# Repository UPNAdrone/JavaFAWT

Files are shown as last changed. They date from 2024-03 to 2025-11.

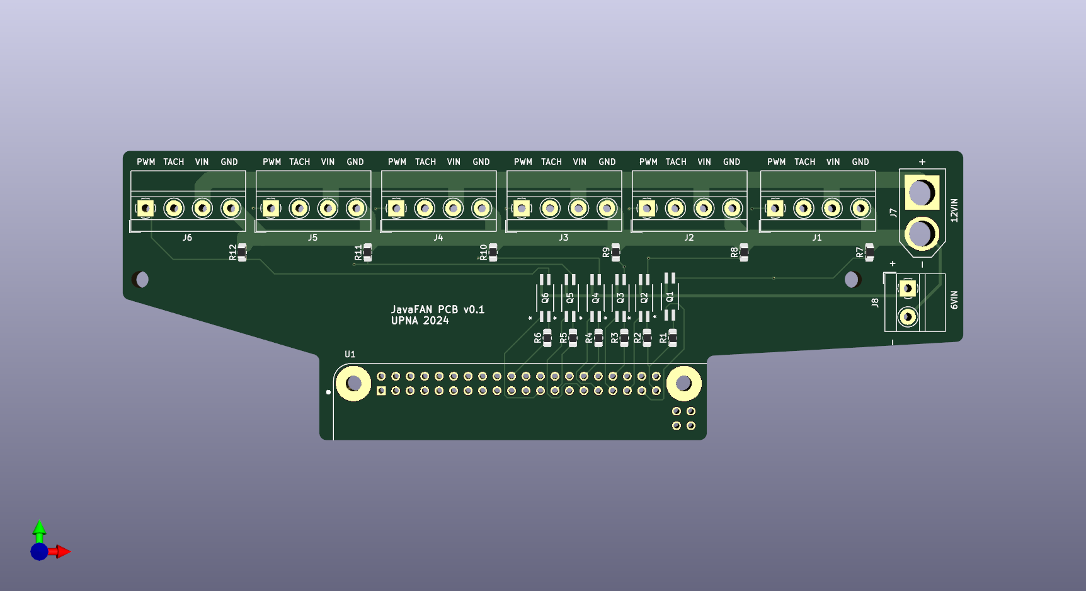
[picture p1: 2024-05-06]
hardware/module/electronics/pcb-test.png

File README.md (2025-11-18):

# JavaFAWT
JavaFAWT is a fan-array-wind tunnel (FAWT) open-source software and hardware architecture developed by the drones lab of Universidad Pública de Navarra. It includes diagrams and PCB layouts for electronics, CAD designs for hardware, and source files for running and adapting the software. 
## Introduction


The proposed control scheme follows a wireless server-client architecture. A Java GUI is provided for the control station (server) to connect and command each fan, organized in series of modules. Each module is managed by a single Raspberry Pi client (currently tested with Raspberry Pi 3, 4, Zero 2 w), which receives the fan speed control messages from the server via a wireless WebSocket. The client receives the message, identifies its connected fans, and converts the speed signal to a PWM output for each fan, allowing for precise individual control of an indefinite number of fans. Thanks to the custom PCB interface, an external power supply can be used for each module, and a single control power source is used to elevate the 3.3V PWM control signal for each and every fan up to a standard required voltage.

### Features
* Modular low-cost FAWT architecture.
* Individual or multiple fan speed control through a simple unified interface.
* Websockets protocol implemented for wireless communication with each fan module.
* User-programmable automatic speed sequences via .CSV files for repeatability and reproducibility of experiments.

## Relevant links
Bill of Materials (BOM) can be found [here](https://github.com/UPNAdrone/JavaFAWT/blob/main/hardware/Bill%20of%20Materials.xlsx)

PCB Manufacturing project can be found [here](https://www.pcbway.com/project/shareproject/JavaFAWT_PCB_v0_1_1426b5d5.html)

## How to install & run
Detailed instructions for installing and running the software can be found [here](https://github.com/UPNAdrone/JavaFAWT/blob/main/documentation/private/docs/installation.md).

A Tutorial/Manual of use can be found [here](https://github.com/UPNAdrone/JavaFAWT/blob/main/documentation/private/docs/installation.md).

## Files structure
- Documentation
  - private
    - docs -> .md files for generating public documentation site.
    - site -> compiled documentation website for dev purposes.
  - public -> compiled documentation website for public purposes.
- Examples -> provided examples.
- Hardware
  - module -> All the components required to assemble a single module.
  - testing_equipment -> Other components developed for testing.
- Software
  - clientCode -> Python PWM client
  - functionalities -> example functionalities provided for automatic fan control.
  - pythonCode -> Python client file for controlling the fans from the Raspberry Pi.
  - serverCode -> JavaFAWT server software.

## Dataset for inverse flow control
Our recorded dataset consists of approximately 45,176 samples recorded with our experimental 6x4 wind tunnel. It includes two CSV files: one for relative pressures (directly extracted from the nanoDAQ LTS-32 pressure scanner readings), one for velocities (extracted by converting the relative pressure, temperature and density values to velocity). The dataset can be found in Hugging Face: [https://huggingface.co/datasets/UPNAdrone/WindTunnel](https://huggingface.co/datasets/UPNAdrone/WindTunnel)

## Work in progress
* Fan speed feedback is currenly under development.
  
## Licensing
JavaFAWT is made available under the [MIT License](https://opensource.org/licenses/MIT). You are free to use, modify, and distribute this module in accordance with the terms of the MIT License.

### Reference and Citation
If you use this module for research, please consider citing our paper to acknowledge its contribution:

```bibtex
@article{pending,
  title={},
  author={},
  journal={},
  volume={},
  pages={},
  year={},
  publisher={}
}
```

---



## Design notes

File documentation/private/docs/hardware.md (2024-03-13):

# How to build a FAWT

URL example: [mkdocs.org](https://www.mkdocs.org).

## Commands

* `mkdocs new [dir-name]` - Create a new project.
* `mkdocs serve` - Start the live-reloading docs server.
* `mkdocs build` - Build the documentation site.
* `mkdocs -h` - Print help message and exit.

## Project layout

    mkdocs.yml    # The configuration file.
    docs/
        index.md  # The documentation homepage.
        ...       # Other markdown pages, images and other files.

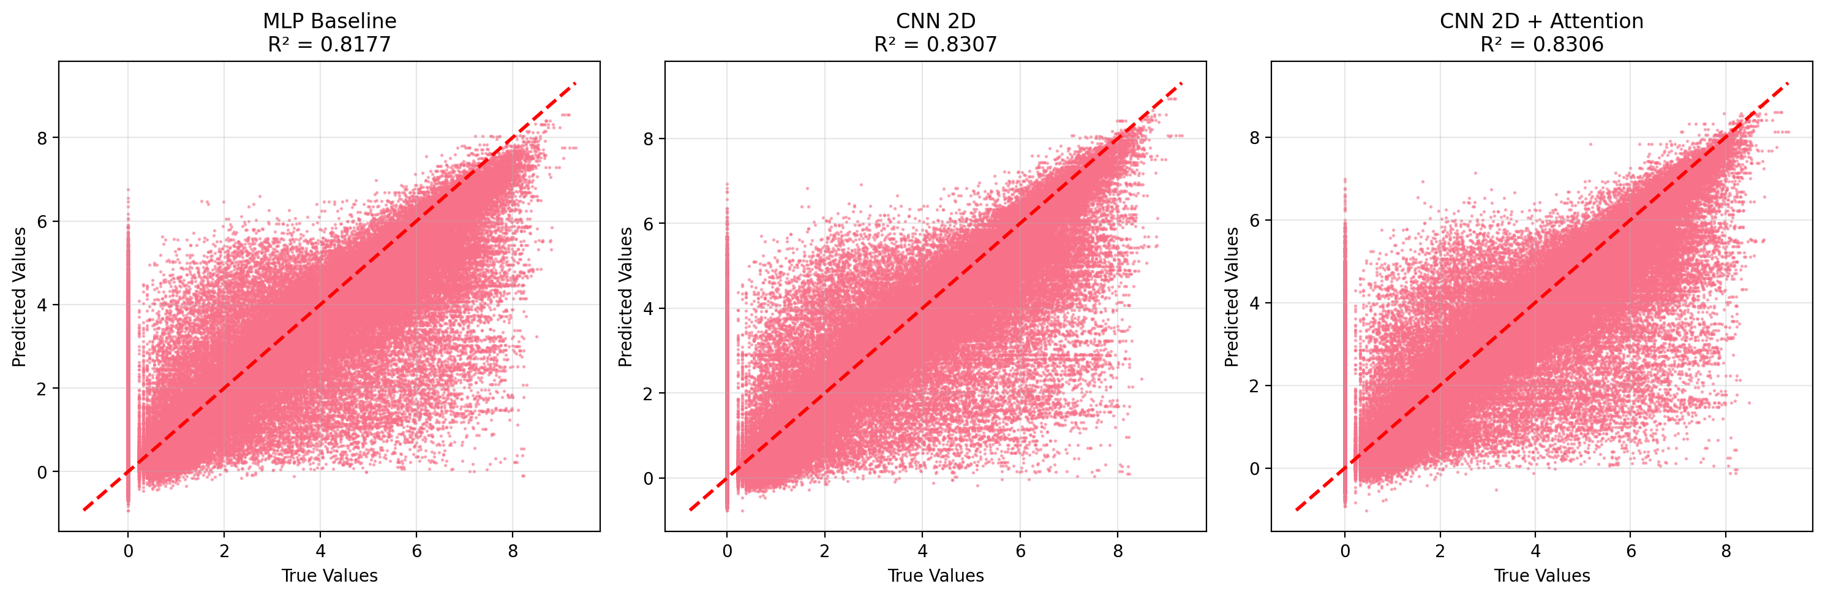
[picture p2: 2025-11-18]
inverse_control/unified_comparison/predictions_vs_true.png

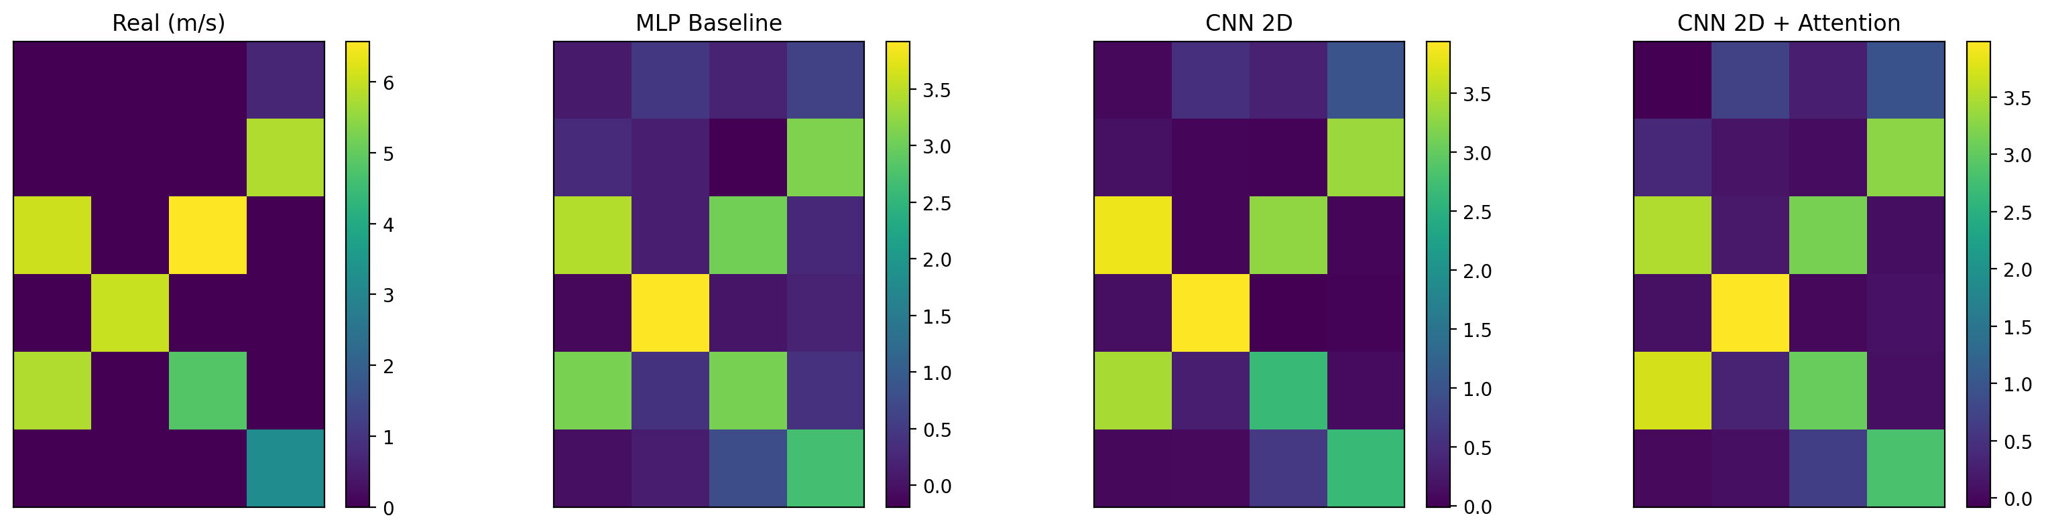
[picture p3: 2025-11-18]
inverse_control/unified_comparison/18cm/sample_heatmaps_7_idx_6357.png

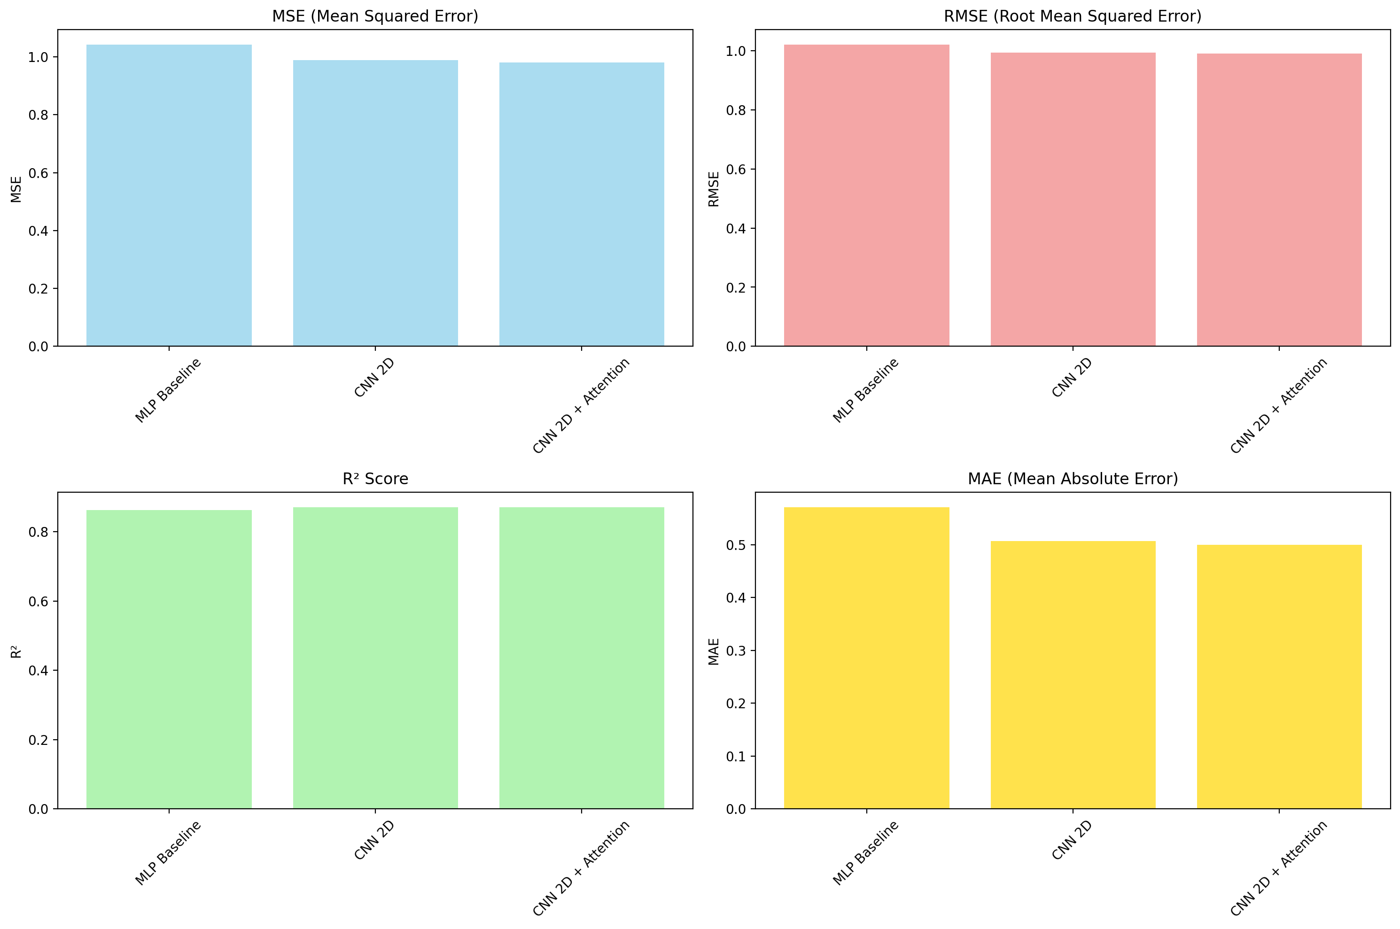
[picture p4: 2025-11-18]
inverse_control/unified_comparison/38cm/metrics_comparison.png

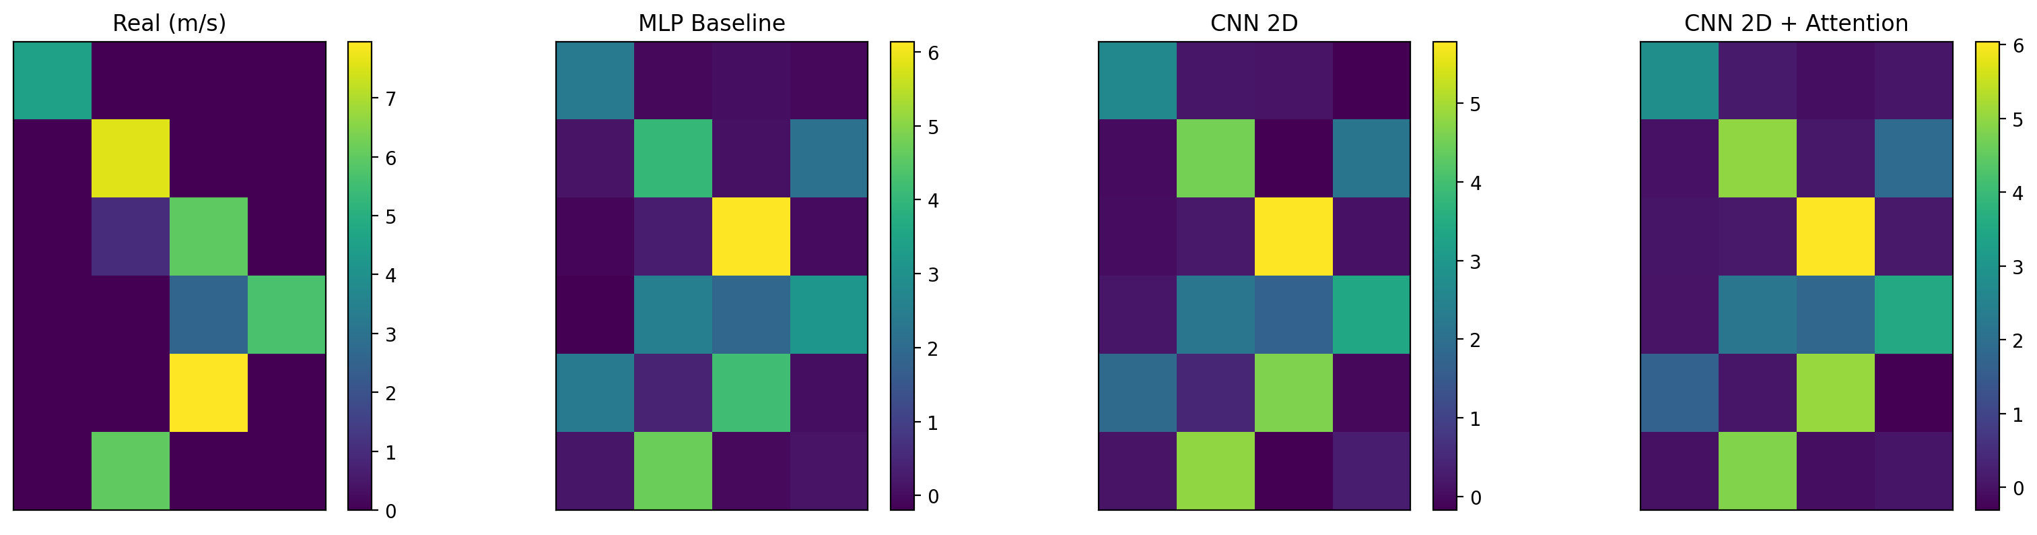
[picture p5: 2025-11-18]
inverse_control/unified_comparison/48cm/sample_heatmaps_0_idx_0.png

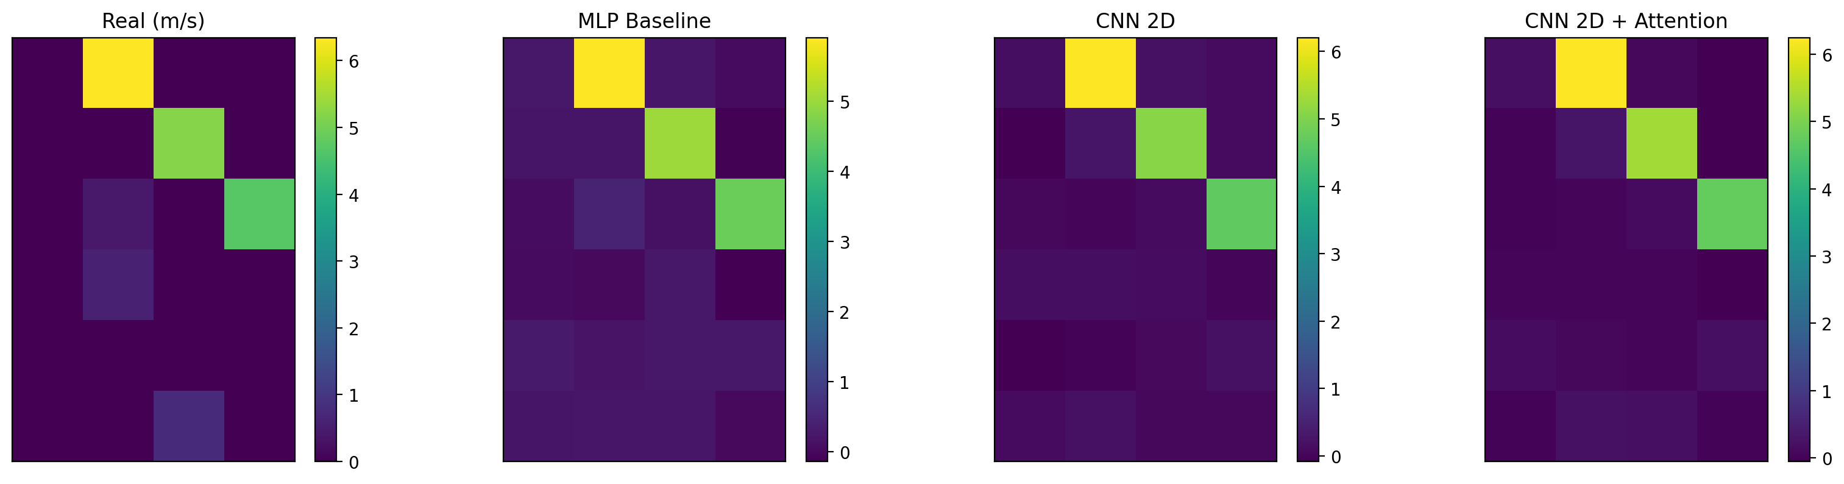
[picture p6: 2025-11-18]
inverse_control/unified_comparison/18cm/sample_heatmaps_4_idx_3632.png

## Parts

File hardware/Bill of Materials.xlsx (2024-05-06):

 |  |  | Est. total per module | 255.04
Single module
Group | Component | Qty | Approx. Unitary Cost (€) | Approx. Total Cost (€) | Description | Link
Structural Unit | Sheet metal structure | 1 | 20 | 20 | Galvanized steel (1 mm), Laser cut, press bending (ordering 4 units) | https://github.com/UPNAdrone/JavaFAWT/blob/main/hardware/module/structure_sheet_metal_folding.SLDPRT
Structural Unit | Cable guides | 3 | 1 | 3 | 3D printable. | https://github.com/UPNAdrone/JavaFAWT/blob/main/hardware/module/cable-management.SLDPRT
Structural Unit | Bgears b-Blaster 140x38 (PWM) | 6 | 30 | 180 | 308 cfm, 33 W. Make sure to order PWM variant. Includes screws. | https://www.bgears.com/b-blaster/
Structural Unit | Raspberry Pi Zero 2W | 1 | 20 | 20 | Client-side. One for each module. Make sure to order WiFi variant (W). | https://www.raspberrypi.com/products/raspberry-pi-zero-2-w/
Structural Unit | 200W minimum PC Power supply | 1 | 17 | 17 | Tacens Anima APIII500 PC ATX 500 W 12V | https://www.amazon.es/Tacens-APIII500-Alimentaci%C3%B3n-Tecnolog%C3%ADa-Ultra-silencioso/dp/B09V5G5R4G?sp_csd=d2lkZ2V0TmFtZT1zcF9hdGY
PCB | JavaFAWT PCB | 1 | 5 | 5 | 147.5x50.8mm 2 Layers,Thickness:1.6 mm, Finished copper:2,Surface finish:HASL with lead | https://www.pcbway.com/project/shareproject/JavaFAWT_PCB_v0_1_1426b5d5.html
PCB | SMD 1.6K Resistor (1%) | 6 | 0.02 | 0.12 | 250 mW, 0805, 1% | https://es.farnell.com/koa-speer-electronics/rk73h2attd1601f/res-1k6-1-0-25w-0805/dp/3548800
PCB | SMD 430 Resistor (1%) | 6 | 0.02 | 0.12 | 250 mW, 0805, 1% | https://es.farnell.com/koa-speer-electronics/rk73h2attd4300f/res-430r-1-0-25w-0805/dp/3548858
PCB | Optocoupler 1 channel 4 pins | 6 | 0.7 | 4.2 | Transistor output, 1 channel, SSOP, 4 pins, 50mA, 3.75 kV, 80% | https://es.farnell.com/on-semiconductor/hmha2801ar2/optocoupler-transistor-3-75kv/dp/2453213?st=HMHA2801
PCB | PCB terminal block 2 Ways 5 mm | 14 | 0.4 | 5.6 | Multicomp Pro MC000026, 5 mm, 2 ways, 26 AWG, 12 AWG, Screw | https://es.farnell.com/multicomp/mc000026/bloque-terminal-pcb-5-mm-2-v-as/dp/2007995?MER=sy-me-pd-mi-acce
Server | Any PC capable of running Java | 1 | - |  | - | -

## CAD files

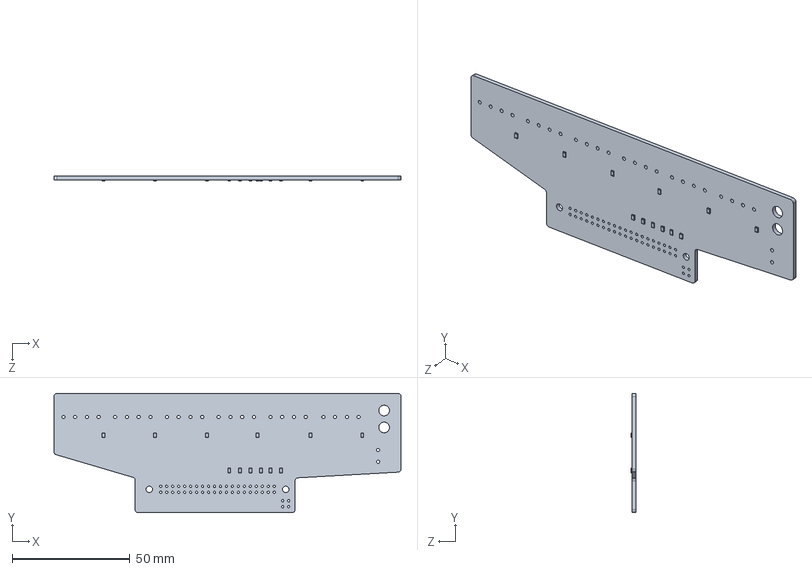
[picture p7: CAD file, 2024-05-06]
hardware/module/electronics/pcb-v01.SLDPRT
147.5 x 50.8 x 2.10 mm

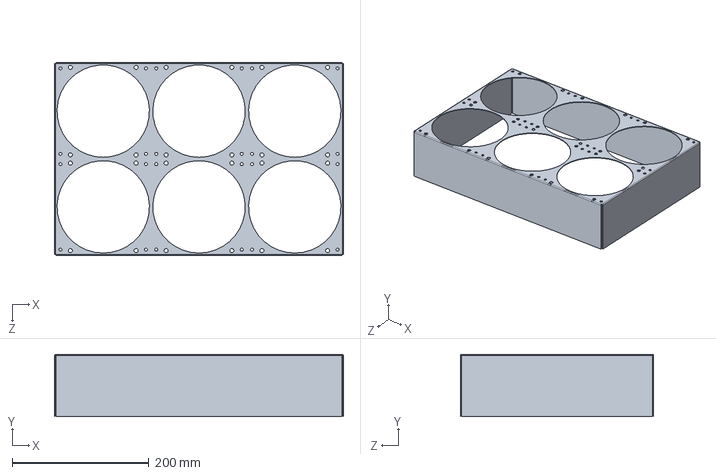
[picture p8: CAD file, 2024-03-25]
hardware/module/structure_sheet_metal_folding.SLDPRT
422.5 x 91.0 x 282.5 mm

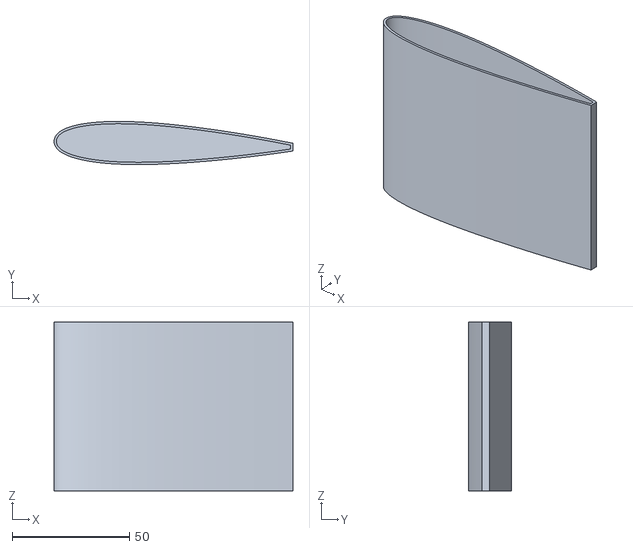
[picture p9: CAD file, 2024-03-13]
hardware/testing_equipment/NACA0012_3dprintable.STL
102.0 x 18.5 x 72.0

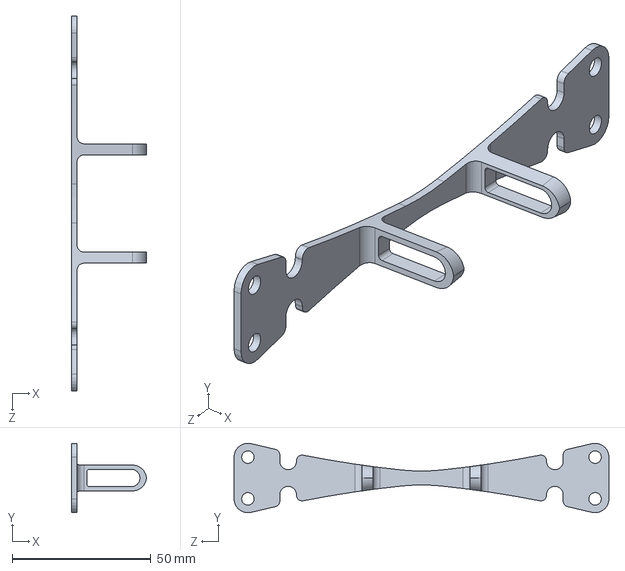
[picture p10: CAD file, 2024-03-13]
hardware/module/cable-management.SLDPRT
27.0 x 25.0 x 135.0 mm

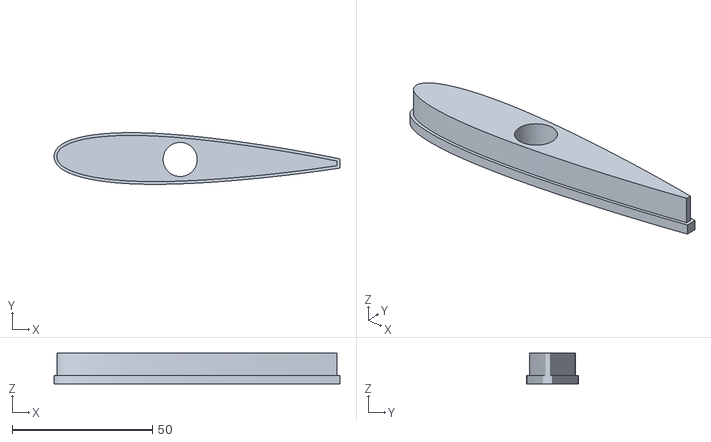
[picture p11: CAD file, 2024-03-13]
hardware/testing_equipment/NACA0012-cover_3dprintable.STL
102.0 x 18.4 x 11.0

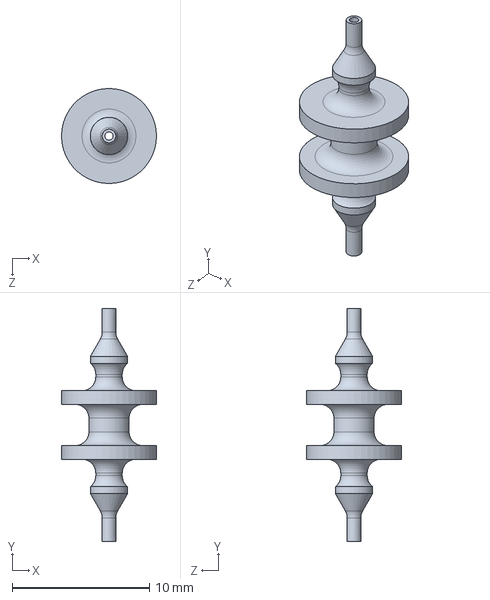
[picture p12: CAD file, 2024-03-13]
hardware/testing_equipment/profile-fitting.SLDPRT
6.93 x 17.0 x 6.93 mm

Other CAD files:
hardware/module/enclosure_sheet_metal_manufacturable.STEP
hardware/testing_equipment/NACA0012.SLDPRT
hardware/module/cable-management_3dprintable.STL
hardware/testing_equipment/NACA0012-cover.SLDPRT

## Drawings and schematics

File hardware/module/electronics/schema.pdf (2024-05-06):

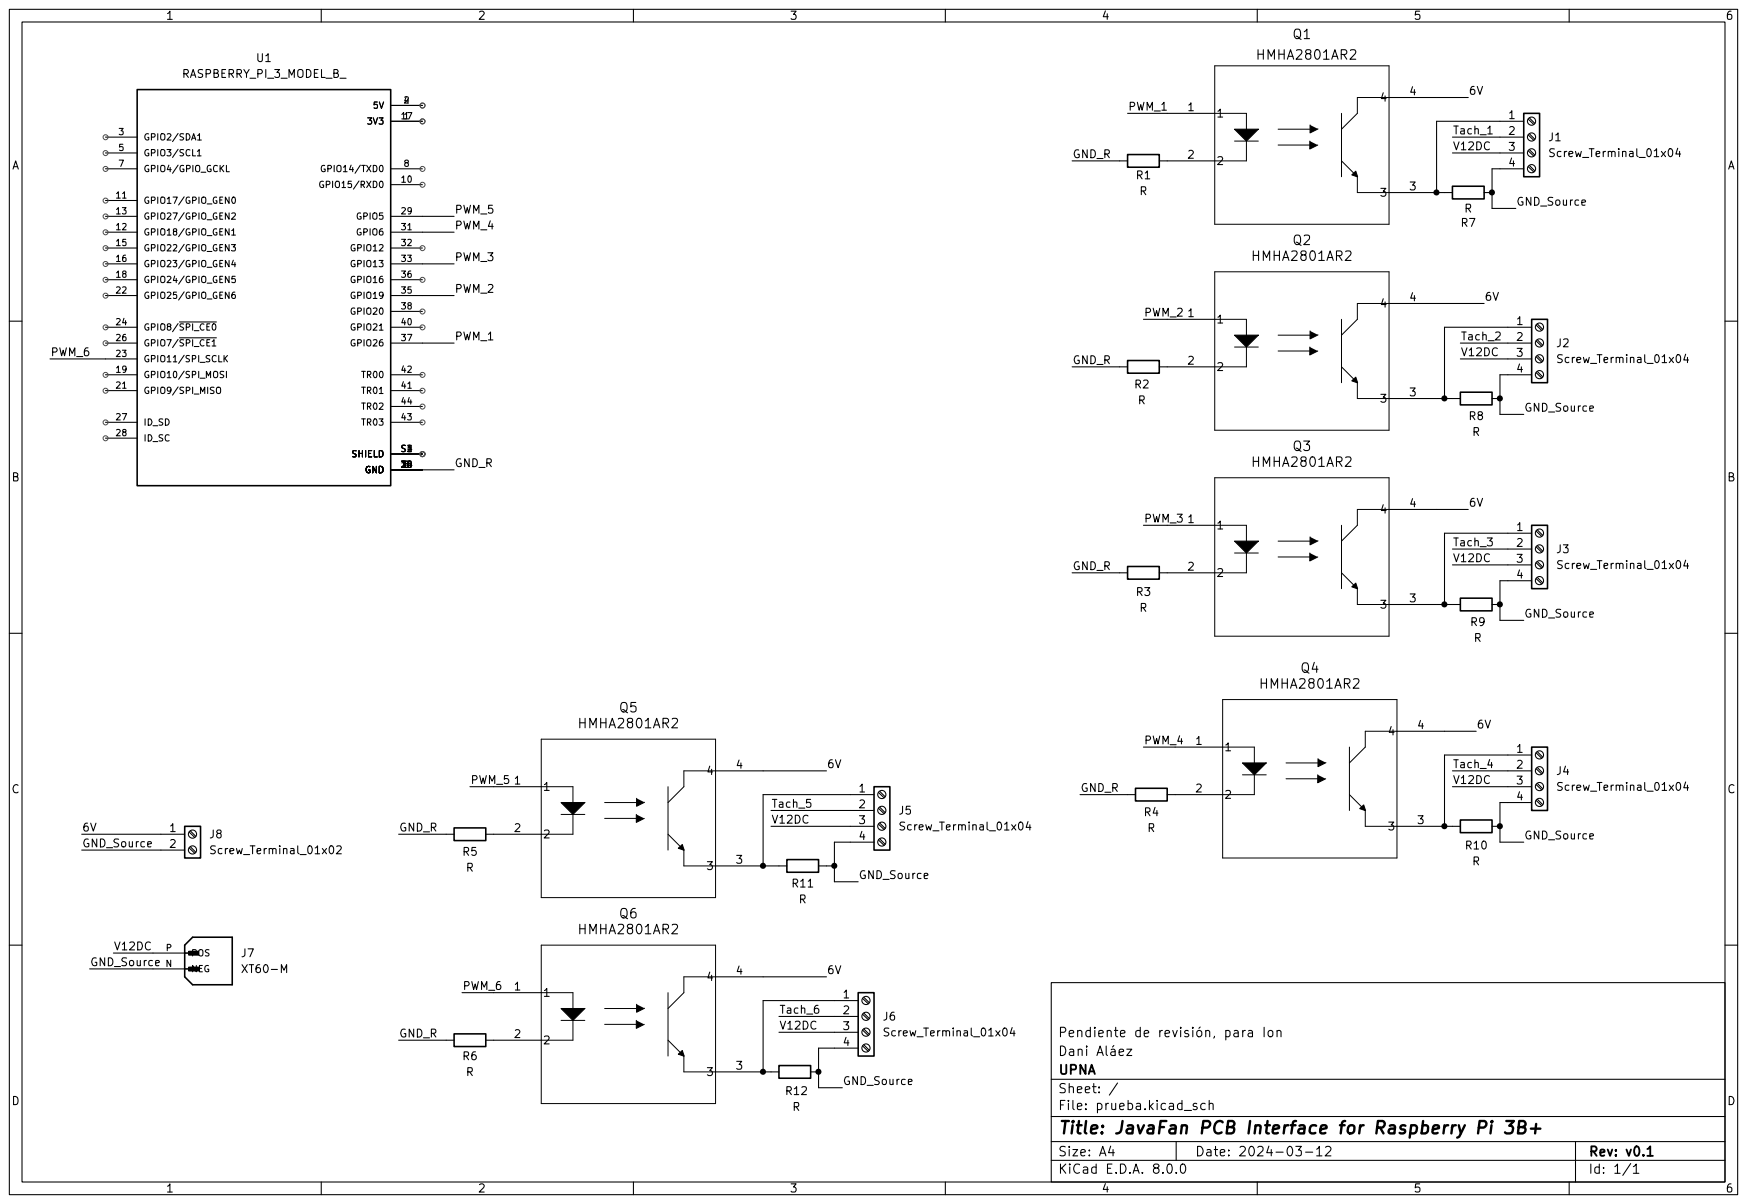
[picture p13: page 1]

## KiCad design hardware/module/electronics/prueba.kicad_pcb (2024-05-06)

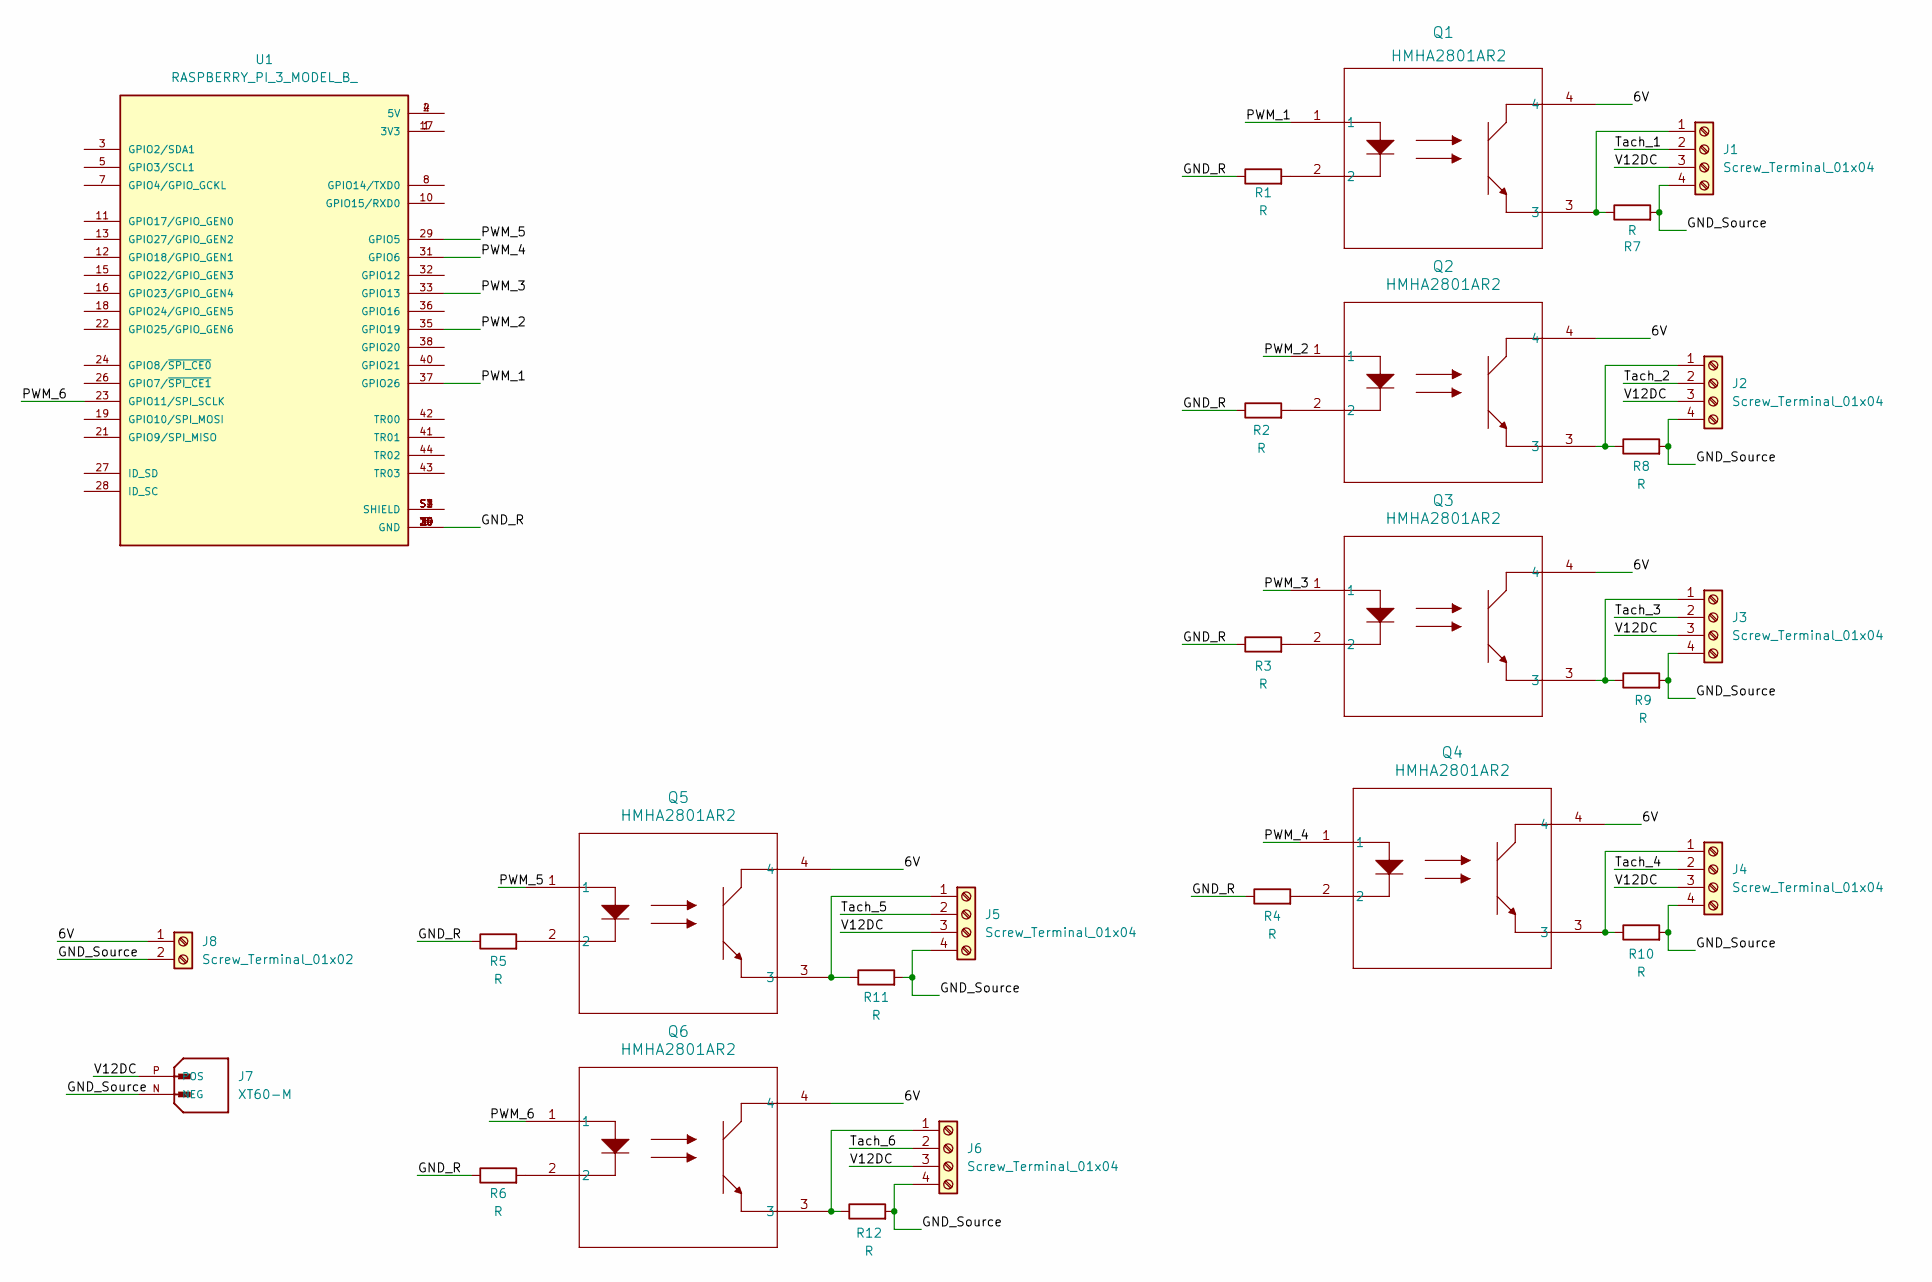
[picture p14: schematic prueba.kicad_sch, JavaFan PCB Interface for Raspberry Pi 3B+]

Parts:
J1, J2, J3, J4, J5, J6: Screw_Terminal_01x04; TerminalBlock_MetzConnect_Type011_RT05504HBWC_1x04_P5.00mm_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
J7: XT60-M; AMASS_XT60-M; PARTREV V1.2
J8: Screw_Terminal_01x02; TerminalBlock_MetzConnect_Type011_RT05502HBWC_1x02_P5.00mm_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
Q1, Q2, Q3, Q4, Q5, Q6: HMHA2801AR2; MFP4_100AL_OSI-M
R1, R2, R3, R4, R5, R6, R7, R8, R9, R10, R11, R12: R; R_0805_2012Metric_Pad1.20x1.40mm_HandSolder
U1: RASPBERRY_PI_3_MODEL_B_; MODULE_RASPBERRY_PI_3_MODEL_B_; PARTREV N/A

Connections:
/6V: J8.1, Q1.4, Q2.4, Q3.4, Q4.4, Q5.4, Q6.4
/GND_R: R1.1, R2.1, R3.1, R4.1, R5.1, R6.1, U1.6 (GND), U1.9 (GND), U1.14 (GND), U1.20 (GND), U1.25 (GND), U1.30 (GND), U1.34 (GND), U1.39 (GND)
/GND_Source: J1.4, J2.4, J3.4, J4.4, J5.4, J6.4, J7.N (NEG), J8.2, R7.2, R8.2, R9.2, R10.2, R11.2, R12.2
/PWM_1: Q1.1, U1.37 (GPIO26)
/PWM_2: Q2.1, U1.35 (GPIO19)
/PWM_3: Q3.1, U1.33 (GPIO13)
/PWM_4: Q4.1, U1.31 (GPIO6)
/PWM_5: Q5.1, U1.29 (GPIO5)
/PWM_6: Q6.1, U1.23 (GPIO11/SPI_SCLK)
/Tach_1: J1.2
/Tach_2: J2.2
/Tach_3: J3.2
/Tach_4: J4.2
/Tach_5: J5.2
/Tach_6: J6.2
/V12DC: J1.3, J2.3, J3.3, J4.3, J5.3, J6.3, J7.P (POS)
unnamed: J1.1, Q1.3, R7.1
unnamed: J2.1, Q2.3, R8.1
unnamed: J3.1, Q3.3, R9.1
unnamed: J4.1, Q4.3, R10.1
unnamed: J5.1, Q5.3, R11.1
unnamed: J6.1, Q6.3, R12.1
unnamed: Q1.2, R1.2
unnamed: Q2.2, R2.2
unnamed: Q3.2, R3.2
unnamed: Q4.2, R4.2
unnamed: Q5.2, R5.2
unnamed: Q6.2, R6.2
unnamed: U1.1 (3V3), U1.17 (3V3)
unnamed: U1.2 (5V), U1.4 (5V)
unnamed: U1.S1 (SHIELD), U1.S2 (SHIELD), U1.S3 (SHIELD), U1.S4 (SHIELD)

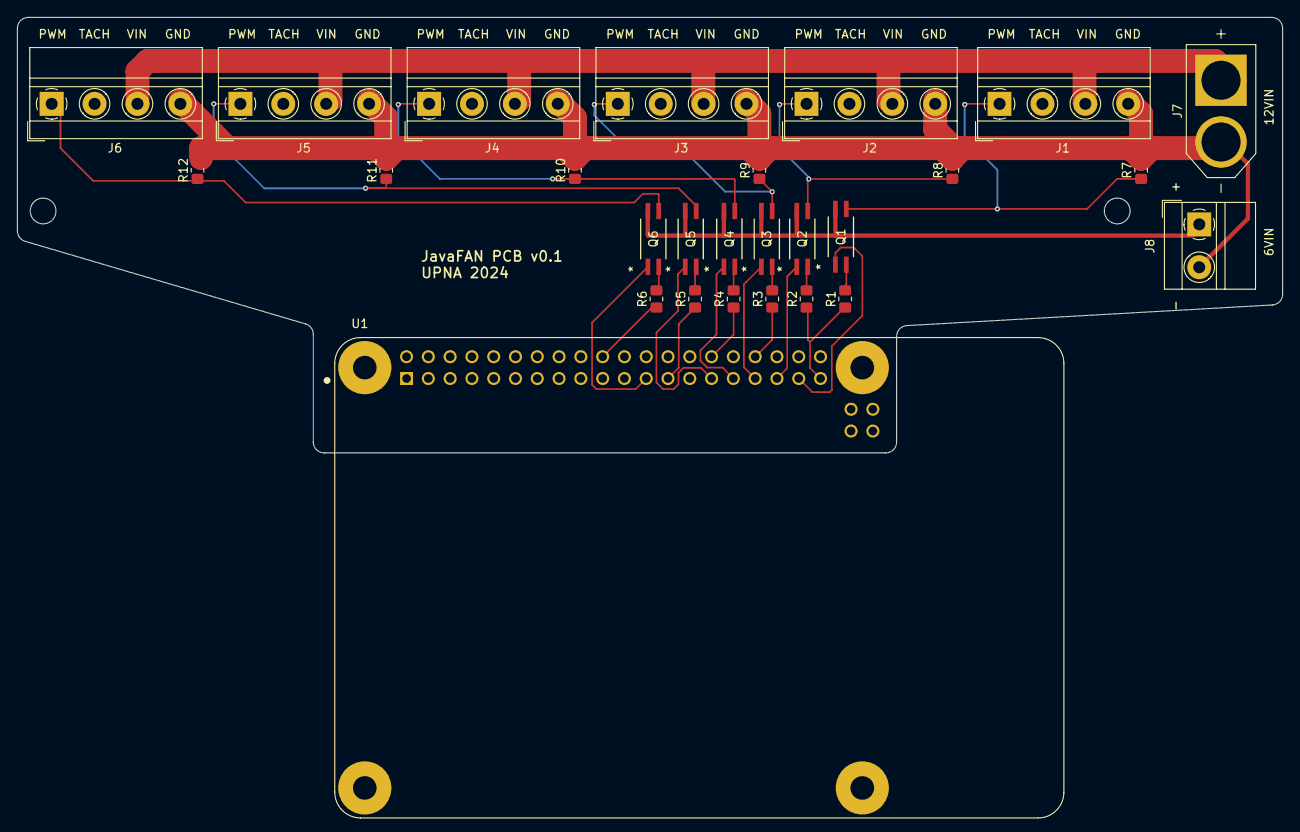
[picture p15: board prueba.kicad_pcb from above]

Board: 2 copper layers, 147.5 x 50.8 mm, 27 parts (0 on the bottom side), 25 nets.

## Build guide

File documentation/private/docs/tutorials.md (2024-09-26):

# Tutorial / Manual of use

The following tutorial is just a guidance to the use of the software. If there is something that is not understood in the tutorial, it is recommended to visit the software documentation. There you will find much more information about each class.

In case you need to change some connection protocol, ip address, port number,... just open the software documentation and there you will find where to change it.

In any other case, please contact us.

## INTRODUCTION

To control the fan modules there is needed a computer and some raspberries. The raspberries are the ones that modify the speed of the fans, but we want to do these modifications from our computer. Hence, the computer has to be connected to each one of the raspberries.

## CLIENT

### Raspberry pi settings (repeat for each raspberry)
1.  The clients that will be physically connected to the fan modules are raspberries. You can use either raspberries pi 0, 3 or 4. In my case I have tried with the three of them. To configure them you can use the “Raspberry Pi Imager” app, following the instructions of this document, https://bricolabs.cc/wiki/guias/guiadeinicioraspberrypi2021 . Make sure you put a different hostname for every raspberry, so that later you can distinguish them.

2.  After that, you will connect your raspberry to the current. Now, open the “Advanced IP Scanner” app to scan all the active ip addresses on your net. If the configuration has been done correctly you will see your raspberries with their hostnames and their ip addresses.

3.  Now, using the “PuTTY” app, connect to your raspberries introducing their ip address. When you do that, a raspberry terminal window will open. There you can navigate through its files and folders.

4.  Go to “/software/clientCode” folder and there you will find a single file called pwm_client. This file is used for the raspberry to connect to the server.

5.  On the raspberry’s terminal, find a location to save this file (for example on /desktop). Once you found it, type “nano pwm_client.py” and paste the content of the pwm_client.py in this file. Make sure you know the location of the file. Repeat it in all the raspberries.

6. To execute the file you need some previous installations (type the following on this directory):
    * sudo apt install python3
    * pip3 install RPi.GPIO

7. Your raspberries are ready to work. Do not forget that it requires 5V to work properly. More volts can break it.

### Connect fans to Raspberry (repeat for each raspberry)
1.  Mount the design for the connection of the cables on the raspberry. It is put on its pins.

2. There are two places to connect current of 12V and 6V.

3. Then you will find 6 different modules. Each of them corresponds to a fan. Each fan has cables with different colors: PWM (blue), TACH (yellow), VIN (red) and GND (black) to be connected. This link can help identify where each cable goes (https://mans.io/files/viewer/1709981/1 ) by looking at the colors. The first fan is the one closer to the 12V current. Then connect them in order.

### Connection (if the Raspberry pi settings has been already done)
1.  Connect the raspberries to the current. 

2.  Open Advanced IP Scanner to look for their IP addresses and use PuTTY to connect to each one of them.

3.  In the terminals, search for the location of pwm_client.py. To execute it you need to introduce the IP address and a port number of the server. So, before executing the file, make sure the server is active and listening for clients.

4.  Next, once in the folder of pwm_client.py, type the following line to execute the client: python pwm_client.py “server_ip” “port”. (for example: python pwm_client.py 192.168.1.33 125)

5.  If the connection is successful, it will be printed, “I am client x”, being x the number of clients assigned to you. You are now connected to the server.

6.  From now on, you won’t have to use the raspberries anymore. During the execution, the raspberries will be printing the messages they are receiving in the terminal, just if necessary.

##  SERVER
1.  Enter the “/software/serverCode/target” folder.

2.  Execute the .jar file called "serverCode-1.0-SNAPSHOT.jar”. You may need to do it through the terminal.

3.  A window called FAN CONNECTION will open. There you will see your server ip and your server port (comment1). Below, is a list where the connected clients will show up. When a client successfully connects to the server, it will appear on the list.
Once you see all the clients connected, you can click on the Ready button to continue.

4.  Two new windows will open. The window called SPEED SCHEMA shows the changing speed of the different active fans. It works with red colored circles. When a specific fan increases its spinning speed, the circle in its position will become bigger. The same happens with all the other positions of the fans. This window is just a visual representation of the speeds of all the active fans.

5.  Moreover, the FAN CONTROL window is the one used to control the fans. There are two different ways to control them.
    - Manually: At the left side of the window, you can see the Fans schema, where you will be able to select your active fans (comment2). You can select several fans by clicking on them. Once you select one of them, on the upper right part, you will see its current speed. The selected fans will be in green color, while the other ones are in white (the inactive fans are in red).
Use the scrolling bar to set the speed you want for the selected fans. Once set, click on the Update button to send the speed to the clients. The selected fans will automatically start spinning at that speed and on the SPEED SCHEMA you will see a change in its circle dimensions (depending on the new speed). To stop all the fans, click on the Stop All button.
    - By a functionality file: If you don’t want to manually set every fan speed you can also use a functionality file. The file must be in format .xlsx to be read correctly. The first column is for the time and the next columns are for the fan's speed. You have some examples in the “/software/functionalities” folder. To use it, click on the Add Functionality Button on the window. Drag and drop the file. Once added you will see its name below. Now you have two options:
        - Real execution: If you click on the Execute Functionality button, the fans will receive their new speeds and the functionality will execute in real time. To stop it you can click on Stop Execution, but notice that this button just stops the reading of the files, the fans will keep spinning at the last speed they received.. During this execution, the manual fan control will be disabled.
        - Preview execution: If you click on Execute Preview the fans will not change. A window like SPEED SCHEMA will open, and there you will be able to see what will happen to the fans if you execute the functionality. To close it, just close the window.

6. Apart from this, you can also click on Show Pressure to see the pressure values in real time on a window. For this, you will need a specific pressure sensor. The first time you open it you will have to introduce its IP address and its port number. In our case we have used a nanodaq-lts-32, that has 32 reading points.

7. Before closing the program don’t forget to Stop All the fans. Otherwise, they will keep the last speed value you gave them, and as soon as they connect to current, they will spin at this speed.

##  FUNCTIONALITY FILES

1. In the software folder, inside functionalities, there are some example files that can be used to execute the fans with them.

2. In case you do not want to use them, you can create new ones or just modify the existing ones. But remember that they need to have the .svg extension.

3. The files are read row by row. Each row represents a speed update. The first column is the time (in milliseconds) you want the fans to be spinning at these speeds, while the other columns are the speeds of each fan (in percentage), in order.
 
### Comments
- Comment 1
The default server port is the 125. In case you want to change it, go to the serverCode project, in the folder “x”. Open the class “Main.java”. In the line 14, replace “125” with the port you wish.

- Comment 2
Once pressed the ready button. The software will check how many clients are connected to the server to display their fans. If only one client is connected, the only available fans will be from 1 to 6. If there are two, from 1 to 12, and so on. The available fans appear in white color and can be clicked, while the not available ones appear in red color and cannot be clicked.

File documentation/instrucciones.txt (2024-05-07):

python -m mkdocs serve (dentro de private) te genera la página en local que se actualiza conforme vas editando la documentación. 
Cuando terminas, si haces python -m mkdocs build te compila la página web y genera los archivos para subir al servidor (lo correspondiente a la carpeta public)

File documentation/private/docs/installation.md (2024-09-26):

# How to Install the server

1. Ensure Java is Installed:
    * The java version must be 17 or above
    * You can see you java version by typing "java -version" on the windows or linux terminal
    * Install Java for Windows:
        - Visit https://www.java.com/download.
        - Download the appropriate Java installer for your system.
        - Run the installer and follow the on-screen instructions to complete the installation.
    * Install Java for Linux:
        - Open the terminal and type "sudo apt install openjdk-17-jdk"
        - After that java will be installed

2. Download or Clone the JavaFAWT Project: Either download the project as a ZIP file or clone the repository to your local machine.

3. Navigate to the Target Folder:

4. Open the project directory and go to software/serverCode/target/.

5. Run the Application:
    * Open a terminal in the target folder.
    * Run the following command: java -jar serverCode-1.0-SNAPSHOT.jar

6. The Program Will Now Execute: The command will launch the program, and it should start running successfully.

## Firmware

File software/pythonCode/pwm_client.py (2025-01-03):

# Program: pwm_client.py
# User: Mintxoo
# Date: 05/12/2023
# Version: 1

import socket
import RPi.GPIO as GPIO


def splitCommas(inputStr, myFans, clientNum):
    array = list(map(int, inputStr.split(",")))
    print()
    for i in range(6):
        speed = array[i + 6 * (clientNum - 1)]
        myFans[i].ChangeDutyCycle(speed)
        print(i,": ",speed)	


def main():
    import sys

    GPIO.setmode(GPIO.BOARD)

    if len(sys.argv) < 3:
        print("Specify an IP and a port")
        sys.exit(-1)

    server_ip = sys.argv[1]
    server_port = int(sys.argv[2])
    client_socket = socket.socket(socket.AF_INET, socket.SOCK_STREAM)

    try:
        client_socket.connect((server_ip, server_port))
        print("Waiting for connectivity...")

        client_number = int(client_socket.recv(1024).decode())
        print(f"I am client {client_number}")

        my_fans = [0] * 6
        message = "a"

        GPIO.setup(37, GPIO.OUT)
        my_fans[0] = GPIO.PWM(37, 5000)
        GPIO.setup(35, GPIO.OUT)
        my_fans[1] = GPIO.PWM(35, 5000)
        GPIO.setup(33, GPIO.OUT)
        my_fans[2] = GPIO.PWM(33, 5000)
        GPIO.setup(31, GPIO.OUT)
        my_fans[3] = GPIO.PWM(31, 5000)
        GPIO.setup(29, GPIO.OUT)
        my_fans[4] = GPIO.PWM(29, 5000)
        GPIO.setup(23, GPIO.OUT)
        my_fans[5] = GPIO.PWM(23, 5000)

        for i in range(6):
            my_fans[i].start(0)

        while True:
            data = client_socket.recv(1024).decode()
            if data:
                if "Server says: exit" in data:
                    print("EXIT")
                    break

                splitCommas(data, my_fans, client_number)
                client_socket.send(message.encode())

        client_socket.close()

    except Exception as e:
        print(f"Error: {e}")
    finally:
        client_socket.close()


if __name__ == "__main__":
    main()

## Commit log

2024-03-13 Initial structure and hardware parts
    [NACA0012-cover.SLDPRT, NACA0012-cover_3dprintable.STL, NACA0012.SLDPRT, NACA0012_3dprintable.STL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]
2024-03-16 prueba de subida de carpetas mintxo
2024-03-16 subida carpeta functionalities
    [pruebaFuncionalidad.xlsx, pruebaFuncionalidad_2.xlsx]
2024-03-21 Arreglo problemas con la funcionalidad
2024-03-21 Cambio nombres funcionalidades
    [fun_1.xlsx, fun_2.xlsx]
2024-03-21 Librerias
    No me deja hace commit desde el repositiorio asi que subo las librerias en un zip
2024-03-25 Update sheet metal folding structure
    [enclosure_sheet_metal_manufacturable.STEP, structure_sheet_metal_folding.SLDPRT]
2024-03-25 Metidos archivos en software
    [fun_1.xlsx, fun_2.xlsx]
2024-04-22 Tutotial y server actualizados
    [fun_model.xlsx]
2024-04-26 .jar a mejorar y actualizacion totu
    [fun_1.xlsx, fun_2.xlsx, fun_3.xlsx]
2024-05-06 Add electronics folder for PCB
    [pcb-v01.SLDPRT, prueba-B_Cu.gbr, prueba-B_Mask.gbr, prueba-B_Paste.gbr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]
2024-05-06 Add Bill of Materials
    [Bill of Materials.xlsx]
2024-05-13 actualizacion funcionalidades para leerlas bien y .jar hecho
2024-05-16 arreglado funcionalidad
    [fun_1.xlsx, fun_2.xlsx, fun_3.xlsx, fun_model.xlsx]
2024-09-22 vamos a hacer el programa dinamico
2024-09-26 un poqito de todo
2024-10-16 ahi va todo
    [fun_1.csv]
2024-10-22 arreglo conexion sensor presion
2024-10-25 arreglo conexion sensor presiones y mejora visualizacion velocidades
2024-10-26 mas chulas ahora
    [fun_1.csv]
2024-11-18 estructura basica pero que no funciona bien todavia
2024-11-18 funciona el cambio de tabs en speed
2024-11-24 cambio a la hora de mostrar velocidad
2024-11-26 añadido dibujado fans en real (finalmente) falta mejorar el sistema de colores y hacer para que tambien se haga en preview
2024-11-30 eliminados los otros dos proyectos de serverCode, ya solo queda el final que es el bonito. en principio estan todas las funcionalidades incluidas y va bien
2024-12-11 video de la simulacion grabado con la camara
2025-01-13 organizacion y actualizacion de alguna cosilla
    [fun_1.csv, fun_2.csv, fun_3.csv, fun_4.csv]
2025-11-18 Unified training results
    [comparison_by_distance.csv, comparison_table.csv]
2025-11-18 Added unified models and results from training
    [comparison_by_distance.csv, comparison_table.csv]
